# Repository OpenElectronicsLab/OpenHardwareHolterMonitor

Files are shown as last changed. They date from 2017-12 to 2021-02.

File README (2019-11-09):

OpenHardwareHolterMonitor is still in early development

This is not a medical device; it is not intended for diagnosis or treatment
of any medical condition.

http://openelectronicslab.github.io/OpenHardwareHolterMonitor/

LICENSE

Software and firmware is licensed under the GPL version 3 as published by the Free Software Foundataion or (at your option) any later version.

https://www.gnu.org/licenses/gpl-3.0.txt

Hardware designs and documentation are licnesed under the CERN Open Hardware
License version 1.1 or (at your option) any later version.

https://www.ohwr.org/licenses/cern-ohl/license_versions/v1.1

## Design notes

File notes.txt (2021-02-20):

Before we go to print again:
* eyeball review the zones and layers
  * also of the gerbers
* testability
  * what needs to be pulled out as test pads
  * non-tented vias rather than pads?
  * or run all the test to the edge of a board and have a connector?
* JTAG - learn about it?
* KiCAD
   * CI/CD design rule checks? - is it commanline scriptable
   * build KiCAD from source!
   * module community?
   * footprint default (e.g.: 0603 hand-solder), preference file?
   * smarter BoM creation?
      * crawl mouser/digikey for smart defaults for "jelly beans" ?

START HERE:
 * Boston Board has shorts in solder bridges on WROOM, fix this first.

 * Programming the board:
	- we are missing pull-up resistors for ENable (~RESET~) and IO0 (boot)
	- we have not successfully programmed the Wroom using FTDI, unless
		we also by hand toggle the EN & IO0 via jumpers or buttons
	- WROOM32 in Utrecht seems to have a bad reset button
	- Sequence to program the the Wroom:
		0) Connect FT232 USB->Serial to Wroom
			* RX0 to TXD0
			* TX0 to RXD0
			* 3v3 to Power
			* GND to GND
		1) connect IO0 to ground (or hold down boot button)
		2) connect EN to ground briefly (or press and release EN)
		3) hit upload from Arduino IDE as ESP32 Dev Module
	- To make the board go, plan is:
		* solder 10k pull-up resistors between FTDI_V and Q1, Q2
		* solder headers for jumper wires into EN and IO0
		* manually, or via an arduino, toggle the EN, IO0
		* push firmware via USB->Serial

 * Case Design
	- LEDs not considered, light pipes?
	- posts need buttressing
	- hex holes allow nuts to spin, make a tad smaller
	- screw holes are very tight, widen a tad
	- recess touch-proof connectors so they are flush with case or inside
	- compensate for some print warping?
	- gasket for where case sides join?
 * Board design: do we want a programmable LED?
	- allows power LED to be Not Installed / controlled via CPU
	- allows debug blink-codes
 * expose EN and IO0 on FTDI header (P1)?
 * label SW1 with OFF and ON

TODO THIS VERSION (v0.2):

 * double-check that our very tight pick-and-place requirements are realistic
   e.g.: R45
   https://ocmmanufacturing.com/resources/resource/dfm-tip-spacing-components-on-a-pcb/
 * Case Design
 * Software prototype on esp32

 * REV2 board required
   - FIXED in v0.2 : d'oh! v0.1 BT1 is BAT2 & BT2 is BAT1 !!!
   - FIXED in v0.2 : d'oh! v0.1 DGS and CBE are wrong on all the Qs !!!
     - (we de-soldered and rotated and/or jumped around on our v0.1 prototypes)

ORDER PROCESS:
* board dimensions units are in CM not MM at Gold Phoenix

SOMEDAY MAYBE:
  - add solder mask between pins on ADS? (conflicting recommendations)
  - north reserved pin which connects to DGND: smooth awkward copper path

FOR NEXT VERSION:
* more space around mounting holes for screw support placement
* waterproof USB connectors for dust-proofing
* check footprints for corresponding 3D models
* check footprints to see if they are current or from an older version
* Check BOM for duplicates, update schematic accordingly
  - e.g.: "R" vs. "R-device" components which are both 100K Ohm 0603.
* keep a detailed journal of decisions
* add manufacturer-partnumber and manufacturer fields before other annotations
* label all of the networks between components
* finish BOM before starting PCB

CONSIDER:
* Medical Instrument Design and Development on page 265
  suggests switching to sheilded leads for EMI
  (can we use filtering instead?)

* look at standards, determine if external clock is required

* Build a configurably "noisy" and "bad" power-supply for testing
  dial-in out-of-spec for USB: (only 3 or 4 volts or +8 volts)
  configurable amount of 50Hz or 60Hz noise

* Create test signals (configurable fake EEG readings we can feed in)

* simulate defribulator voltage added to test cardiac signals

* test vibration influence with car, train, metro, bus, bike
  compare with swapping-in a tantilum for C8

* Regulater's Capacitor C42 1uF to 10uF should be fine;
  bigger is typically better, but we may get oscillation, need to test

# NOTES ON v0.1 SOT-23 TRANSITORS WITH INCORRECT FOOTPRINTS

## KiCad SOT-23 footprint pin numbering:

      1
          3
      2

## Q1 Q2 : DSS4240T-7

    v0.1 KiCad     actual part

      E                 B
          C                 C
      B                 E

## Q3 Q4 Q5 Q6: 2N7002-7-F

    v0.1 KiCad     actual part

      D                 G
          S                 D
      G                 S

## Q7 Q8 Q9 Q10 Q11 : DMG2305UX-13

    v0.1 KiCad     actual part

      D                 G
          S                 D
      G                 S

--------------------------------------------
Alternated resistors front-to-back in order increase the clearance between
resistors.

--------------------------------------------
esp32	20mA
 +WiFi	90-260mA
ads1298	5mA
ADP7158	4mA -- just one of many low noise linear regulator
sdCard	<1mA
 write	100mA

not tx	~100-200mA
w/ tx	~500mA ... thus efficient power isolation to run off of USB

2 main batteries, but can operate from one, and can swap each out one at a time
 ... simple power-level indicator? push-button and light up to 0-to-3 LEDs?
 ... also indicate on web-page?
1 (regargeable?) coin battery for the real-time-clock
  TODO: look up coin charger schematic on Adafruit?

LP5912-3.0DRVR LDO Voltage Regulator
reference layout suggests big wide ground connecting Pin2 (NC) to thermal pad
with vias to pin 5 (GND)
and use X7R caps anywhere from 1-to-10uF
and a pullup resistor of 10k-100k for PG

charging: conisder the PCP73833 which has cell temperature monitoring
http://www.microchip.com/wwwproducts/en/en027785

18650 batteries are widely available and cost is reasonable
ADS requires 2.7 min; ESP requires 2.8v min; thus no problem.
batteries drop off dramatically around 3 volts:
http://www.candlepowerforums.com/vb/showthread.php?308451-18650-battery-test-with-capacity-curves-for-many-cells

https://www.amazon.de/Nitecore-Intellicharge-Ladeger%C3%A4t-Li-Ion-Batterien/dp/B06XFH6Z5D/ref=sr_1_1?ie=UTF8&qid=1509900684&sr=8-1&keywords=18650+charger+nitecore

https://smile.amazon.com/Battery-Li-Ion-Rechargeable-Button-LR2032/dp/B0058E94O6/ref=sr_1_sc_2?ie=UTF8&qid=1509899680&sr=8-2-spell&keywords=2032+rechagable

V=IR
R=V/I=(1.2V)/(50e-6)=2.4e4V/1A=24000 Ohm
R=V/I=(1.26V)/(47e6)

RO = (R2*RC)/(R2+RC) - (R2*RH)/(R2+RH) = (R2^2*RC - R2^2*RH)/(R2^2 + R2*RC + R2*RH + RC*RH)
R2^2 (RC - RH) = R0 * R2^2 + R0 * R2 * (RC + RH) + R0*RC*RH
0 = -R2^2 * (RC - RH) + R0 * R2^2 + R0 * R2 * (RC + RH) + R0*RC*RH
0 = (R0 - RC + RH) R2^2 + (R0 * (RC + RH)) * R2 + R0*RC*RH
0 = a * R2^2 + b * R2 + c
R2 = -b +/- sqrt(4*a*c - b^2)/(2a)

eric@titan:~/src/build-mysql-server$ python
Python 2.7.13 (default, Nov 24 2017, 17:33:09) 
[GCC 6.3.0 20170516] on linux2
Type "help", "copyright", "credits" or "license" for more information.
>>> from math import *
>>> 10e3 * exp(-3380*(1/(273.15+25.) + 1/(273.15+60))
... )
4.681859273431694e-06
>>> 10e3 * exp(-3380*(1/(273.15+25) - 1/(273.15+60)))
3039.1856851602356
>>> exp(1)
2.718281828459045
>>> exp(1)**2
7.3890560989306495
>>> exp(2)  
7.38905609893065
>>> 10e3 * exp(-3380*(1/(273.15+25) - 1/(273.15+60)))
3039.1856851602356
>>> 10e3 * exp(-3380*(1/(273.15+25) - 1/(273.15+45)))
4903.401159843523
>>> 10e3 * exp(-3380*(1/(273.15+25) - 1/(273.15+0.0)))
28223.725086022154
>>> R0 = 19e3
>>> RH = 3039.1856851602356
>>> RC = 28223.725086022154
>>> RH = 4903.401159843523
>>> b= (R0 * (RC + RH))
>>> a = (R0 - RC + RH)
>>> c =R0*RC*RH
>>> R2 = -b - sqrt(4*a*c - b^2)/(2a)
  File "<stdin>", line 1
    R2 = -b - sqrt(4*a*c - b^2)/(2a)
                                  ^
SyntaxError: invalid syntax
>>> R2 = -b - sqrt(4*a*c - b**2)/(2*a)
Traceback (most recent call last):
  File "<stdin>", line 1, in <module>
ValueError: math domain error
>>> R2 = (-b - sqrt(b**2 - 4*a*c))/(2*a)
>>> R2
149751.3160728841
>>> R2 = (-b + sqrt(b**2 - 4*a*c))/(2*a)
>>> R2
-4064.231162986638
>>> R2 = (-b - sqrt(b**2 - 4*a*c))/(2*a)
>>> R12
Traceback (most recent call last):
  File "<stdin>", line 1, in <module>
NameError: name 'R12' is not defined
>>> R2
149751.3160728841
>>> R1=(5e3 -((R2 * RH)/(R2+RH)))
>>> R1
252.0634995252176
>>> 1/( 1/(273.15 + 25) + 1/3380. * ln(24e3/10e3) )                            
Traceback (most recent call last):
  File "<stdin>", line 1, in <module>
NameError: name 'ln' is not defined
>>> 1/( 1/(273.15 + 25) + 1/3380. * log(24e3/10e3) )
276.77593699164424
>>> log(10)
2.302585092994046
>>> log(exp(1))
1.0
>>> 1/( 1/(273.15 + 25) + 1/3380. * log(24e3/10e3) ) - 273.15
3.6259369916442665
>>> 1/( 1/(273.15 + 25) + 1/3380. * log(5e3/10e3) ) - 273.15
44.416848098726064
>>> 1/( 1/(273.15 + 25) + 1/3380. * log(5e3*.99/10e3) ) - 273.15
44.71700233658754
>>> 1/( 1/(273.15 + 25) + 1/3380. * log(5e3*1.01/10e3) ) - 273.15
44.12023842251841
>>> 1/( 1/(273.15 + 25) + 1/3380. * log(5e3/10e3) ) - 273.15
44.416848098726064
>>> 1.25/50-3
-2.975
>>> 1.25/50e-3
25.0
>>> 1.25/50e-6
25000.0
>>> 1.2/50e-6
23999.999999999996
>>> 1.26/47e-6
26808.510638297874
>>> 1/( 1/(273.15 + 25) + 1/3380. * log(26808e3*1.01/10e3) ) - 273.15
-97.477943830615
>>> 1/( 1/(273.15 + 25) + 1/3380. * log(26808*1.01/10e3) ) - 273.15
0.919435923053868
>>> 1.20/53e-6
22641.509433962263
>>> 1/( 1/(273.15 + 25) + 1/3380. * log(22641*1.01/10e3) ) - 273.15
4.725901928055919
>>> 0.235/53e-6
4433.962264150943
>>> 1/( 1/(273.15 + 25) + 1/3380. * log(4434*0.99/10e3) ) - 273.15
48.34929827083289
>>> 0.265/47e-6
5638.297872340426
>>> 1/( 1/(273.15 + 25) + 1/3380. * log(5638*0.99/10e3) ) - 273.15
41.16716023313063
>>> 1/( 1/(273.15 + 25) + 1/3380. * log(5638*1.01/10e3) ) - 273.15
40.58363861408782

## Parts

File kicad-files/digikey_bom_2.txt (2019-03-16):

#,Manufacturer Part Number,Manufacturer,Description,Customer Reference,Availability,Part Status,Digi-Key Part Number,Packaging,Requested Quantity,Quantity,Unit Price,Extended Price,Manufacturer Lead Weeks,US Tariff Status
1,1043,Keystone Electronics,BATTERY HOLDER 18650 PC PIN,BT1 BT2,8660 Available,Active,36-1043-ND,BULK,2,2,2.30000,$4.60,Manufacturer Standard Lead Time 6 Weeks
2,CC0603JRX7R9BB104,Yageo,CAP CER 0.1UF 50V X7R 0603,C4 C6 C10 C13 C14 C17 C18 C22 C36 C38,668000 Available,Active,311-1779-1-ND,CT,10,10,0.09700,$0.97,Manufacturer Standard Lead Time 16 Weeks
3,CC0603JRNPO9BN101,Yageo,CAP CER 100PF 50V C0G/NPO 0603,C20,1712000 Available,Active,311-1069-1-ND,CT,1,1,0.10000,$0.10,Manufacturer Standard Lead Time 16 Weeks,Tariff Applied
4,CL10B103KB8NCNC,Samsung Electro-Mechanics,CAP CER 10000PF 50V X7R 0603,C21,6216000 Available,Active,1276-1921-1-ND,CT,1,1,0.10000,$0.10,Not Available,Tariff Applied
5,CL21B106KPQNNNE,Samsung Electro-Mechanics,CAP CER 10UF 10V X7R 0805,C12 C40 C42,1822000 Available,Active,1276-1764-1-ND,CT,3,3,0.29000,$0.87,Not Available
6,CC0603JRNPO9BN120,Yageo,CAP CER 12PF 50V C0G/NPO 0603,C1 C2,688000 Available,Active,311-1059-1-ND,CT,2,2,0.10000,$0.20,Manufacturer Standard Lead Time 16 Weeks,Tariff Applied
7,LMK107B7105KA-T,Taiyo Yuden,CAP CER 1UF 10V X7R 0603,C3 C5 C7 C9 C11 C15 C16 C19 C23,1896000 Available,Active,587-1242-1-ND,CT,9,9,0.10000,$0.90,Not Available,Tariff Applied
8,GRM21BD71A226ME44L,Murata Electronics North America,CAP CER 22UF 10V X7T 0805,C8 C39 C41,411000 Available,Active,490-9959-1-ND,CT,3,3,0.48000,$1.44,Not Available
9,TPSE337K010T0050V,AVX Corporation,CAP TANT 330UF 10% 10V 2917,C34 C35 C37,400 Available,Active,478-11252-1-ND,CT,3,3,2.45000,$7.35,Manufacturer Standard Lead Time 10 Weeks
10,C0603C471JAGAC7867,KEMET,CAP CER 470PF 250V C0G/NP0 0603,C24 C25 C26 C27 C28 C29 C30 C31 C32 C33,2701 Available,Active,399-14986-1-ND,CT,10,10,0.07600,$0.76,Manufacturer Standard Lead Time 52 Weeks
11,693072010801,Wurth Electronics Inc.,CONN MICRO SD CARD HINGED TYPE,CON1,1200 Available,Active,732-3820-1-ND,CT,1,1,3.20000,$3.20,Manufacturer Standard Lead Time 17 Weeks
12,BAT60JFILM,STMicroelectronics,DIODE SCHOTTKY 10V 3A SOD323,D1 D2 D3 D6 D10 D12 D13 D14,57000 Available,Active,497-3707-1-ND,CT,8,8,0.39000,$3.12,Manufacturer Standard Lead Time 12 Weeks,Tariff Applied
13,SS10PH10-M3/86A,Vishay Semiconductor Diodes Division,DIODE SCHOTTKY 100V 10A TO277A,D8,24000 Available,Active,SS10PH10-M3/86AGICT-ND,CT,1,1,0.74000,$0.74,Manufacturer Standard Lead Time 12 Weeks,Tariff Applied
14,SMBJ5339B-TP,Micro Commercial Co,DIODE ZENER 5.6V 5W DO214AA,D4 D5,33000 Available,Active,SMBJ5339B-TPMSCT-ND,CT,2,2,0.87000,$1.74,Not Available
15,IN-S63BTA,Inolux,LED AMBER CLEAR 0603 SMD,D7 D11,4000 Available,Active,1830-1071-1-ND,CT,2,2,0.36000,$0.72,Manufacturer Standard Lead Time 8 Weeks
16,LTST-C191KGKT,Lite-On Inc.,LED GREEN CLEAR SMD,D9,1020000 Available,Active,160-1446-1-ND,CT,1,1,0.29000,$0.29,Manufacturer Standard Lead Time 10 Weeks,Tariff Applied
17,1812L050/30PR,Littelfuse Inc.,PTC RESET FUSE 30V 500MA 1812,F1 F2,12618 Available,Active,F4159CT-ND,CT,2,2,1.04000,$2.08,Manufacturer Standard Lead Time 11 Weeks,Tariff Applied
18,CMS1-12-R,Eaton - Electronics Division,CMC 131UH 1.15A 2LN SMD,FL1,2000 Available,Active,513-1683-1-ND,CT,1,1,2.95000,$2.95,Manufacturer Standard Lead Time 16 Weeks
19,M50-3000645,Harwin Inc.,CONN RCPT 12POS 0.05 GOLD PCB,J1,2703 Available,Active,952-1366-5-ND,TUBE,1,1,1.70000,$1.70,Manufacturer Standard Lead Time 10 Weeks
20,12401610E4#2A,Amphenol ICC (Commercial Products),CONN RCP USB3.1 TYPEC 24P SMD RA,J13,37680 Available,Active,12401610E4#2ACT-ND,CT,1,1,2.24000,$2.24,Manufacturer Standard Lead Time 12 Weeks,Tariff Applied
21,629105150521,Wurth Electronics Inc.,CONN RCPT USB2.0 MICRO B SMD R/A,J12,4400 Available,Active,732-5960-1-ND,CT,1,1,2.07000,$2.07,Manufacturer Standard Lead Time 11 Weeks
22,61300711121,Wurth Electronics Inc.,CONN HEADER VERT 7POS 2.54MM,P1,6236 Available,Active,732-5320-ND,BAG,1,1,0.37000,$0.37,Manufacturer Standard Lead Time 14 Weeks
23,2N7002-7-F,Diodes Incorporated,MOSFET N-CH 60V 115MA SOT23-3,Q3 Q4,6681000 Available,Active,2N7002-FDICT-ND,CT,2,2,0.22000,$0.44,Not Available,Tariff Applied
24,2N7002-7-F,Diodes Incorporated,MOSFET N-CH 60V 115MA SOT23-3,Q5 Q6,6681000 Available,Active,2N7002-FDICT-ND,CT,2,2,0.22000,$0.44,Not Available,Tariff Applied
25,DMG2305UX-13,Diodes Incorporated,MOSFET P-CH 20V 4.2A SOT23,Q7 Q8 Q9 Q10 Q11,879607 Available,Active,DMG2305UX-13DICT-ND,CT,5,5,0.45000,$2.25,Manufacturer Standard Lead Time 20 Weeks,Tariff Applied
26,DSS4240T-7,Diodes Incorporated,TRANS NPN 40V 2A SOT-23,Q1 Q2,420000 Available,Active,DSS4240TDICT-ND,CT,2,2,0.44000,$0.88,Manufacturer Standard Lead Time 20 Weeks,Tariff Applied
27,RC0603FR-070RL,Yageo,RES SMD 0 OHM JUMPER 1/10W 0603,R31 R32,4235000 Available,Active,311-0.0HRCT-ND,CT,2,2,0.10000,$0.20,Manufacturer Standard Lead Time 16 Weeks,Tariff Applied
28,ERA-3AEB104V,Panasonic Electronic Components,RES SMD 100K OHM 0.1% 1/10W 0603,R7 R10 R13 R27 R28,1490000 Available,Active,P100KDBCT-ND,CT,5,5,0.35000,$1.75,Manufacturer Standard Lead Time 23 Weeks
29,ERA-3AEB104V,Panasonic Electronic Components,RES SMD 100K OHM 0.1% 1/10W 0603,R37 R38 R41 R42 R43,1490000 Available,Active,P100KDBCT-ND,CT,5,5,0.35000,$1.75,Manufacturer Standard Lead Time 23 Weeks
30,ERT-J1VG103JA,Panasonic Electronic Components,THERMISTOR NTC 10KOHM 3380K 0603,R33 R34,52000 Available,Active,P12014CT-ND,CT,2,2,0.18000,$0.36,Manufacturer Standard Lead Time 7 Weeks
31,ERJ-PB3B1202V,Panasonic Electronic Components,RES SMD 12K OHM 0.1% 1/5W 0603,R5 R6,500 Available,Active,P20094CT-ND,CT,2,2,0.25000,$0.50,Manufacturer Standard Lead Time 18 Weeks
32,ERJ-PB3B1001V,Panasonic Electronic Components,RES SMD 1K OHM 0.1% 1/5W 0603,R9 R12 R35 R36,40000 Available,Active,P19972CT-ND,CT,4,4,0.25000,$1.00,Manufacturer Standard Lead Time 18 Weeks
33,ERJ-PB3B3901V,Panasonic Electronic Components,RES SMD 3.9K OHM 0.1% 1/5W 0603,R8 R11,5000 Available,Active,P20038CT-ND,CT,2,2,0.25000,$0.50,Manufacturer Standard Lead Time 18 Weeks
34,ERA-3AEB331V,Panasonic Electronic Components,RES SMD 330 OHM 0.1% 1/10W 0603,R39 R40,55000 Available,Active,P330DBCT-ND,CT,2,2,0.35000,$0.70,Manufacturer Standard Lead Time 23 Weeks
35,RN73C1J392KBTD,TE Connectivity Passive Product,RES SMD 392K OHM 0.1% 1/16W 0603,R16,3759 Available,Active,A124746CT-ND,CT,1,1,0.80000,$0.80,Manufacturer Standard Lead Time 9 Weeks
36,ERA-3AEB470V,Panasonic Electronic Components,RES SMD 47 OHM 0.1% 1/10W 0603,R1 R2 R3 R4 R14 R15,115000 Available,Active,P47DBCT-ND,CT,6,6,0.35000,$2.10,Manufacturer Standard Lead Time 23 Weeks
37,ERJ-PB3B5101V,Panasonic Electronic Components,RES SMD 5.1K OHM 0.1% 1/5W 0603,R29 R30,5000 Available,Active,P20052CT-ND,CT,2,2,0.25000,$0.50,Manufacturer Standard Lead Time 18 Weeks
38,ASRM2JA51K0,Stackpole Electronics Inc,RES 51K OHM 2W 5% AXIAL,R17 R18 R19 R20 R21 R22 R23 R24 R25 R26,229 Available,Active,ASRM2JA51K0CT-ND,CT,10,10,0.57800,$5.78,Manufacturer Standard Lead Time 11 Weeks
39,JS102011SAQN,C&K,SWITCH SLIDE SPDT 300MA 6V,SW1,36000 Available,Active,401-1999-1-ND,CT,1,1,0.59000,$0.59,Manufacturer Standard Lead Time 13 Weeks,Tariff Applied
40,ADS1298IPAG,Texas Instruments,IC AFE 24BIT SPI 32KSPS 64TQFP,U2,5197 Available,Active,296-27734-ND,TRAY,1,1,38.99000,$38.99,Manufacturer Standard Lead Time 12 Weeks
41,ESP-32,RF Solutions,WIFI802.11B/G/N/E/I BLEUTOOTH CL,U1,7 Available,Active,ESP-32-ND,BAG,1,1,15.68000,$15.68,Manufacturer Standard Lead Time 4 Weeks
42,LP5912-3.3DRVT,Texas Instruments,IC REG LINEAR 3.3V 500MA 6SON,U6,6500 Available,Active,296-44153-1-ND,CT,1,1,1.38000,$1.38,Manufacturer Standard Lead Time 8 Weeks
43,MCP73833T-AMI/UN,Microchip Technology,IC LI-ION/LI-POLY CTRLR 10MSOP,U3 U4,17500 Available,Active,MCP73833T-AMI/UNCT-ND,CT,2,2,0.88000,$1.76,Manufacturer Standard Lead Time 6 Weeks
44,REM3-0505S/A,Recom Power,DC DC CONVERTER 5V 3W,U7,425 Available,Active,945-2224-ND,TUBE,1,1,52.54000,$52.54,Manufacturer Standard Lead Time 16 Weeks
45,TPS2113APWR,Texas Instruments,IC OR CTRLR SRC SELECT 8TSSOP,U5,30606 Available,Active,296-16938-1-ND,CT,1,1,2.41000,$2.41,Manufacturer Standard Lead Time 8 Weeks
46,FK161EIHM0.032768-T5,Fox Electronics,CRYSTAL 32.768KHZ 12.5PF SMD,Y1,5754 Available,Active,631-1486-1-ND,CT,1,1,1.91000,$1.91,Manufacturer Standard Lead Time 13 Weeks

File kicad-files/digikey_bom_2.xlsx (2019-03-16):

# | Manufacturer Part Number | Manufacturer | Description | Customer Reference | Digi-Key Part Number | Quantity/board | Quantity Extra | Quantity
1 | 1043 | Keystone Electronics | BATTERY HOLDER 18650 PC PIN | BT1 BT2 | 36-1043-ND | 2 | 1 | 13
2 | CC0603JRX7R9BB104 | Yageo | CAP CER 0.1UF 50V X7R 0603 | C4 C6 C10 C13 C14 C17 C18 C22 C36 C38 | 311-1779-1-ND | 10 | 5 | 65
3 | CC0603JRNPO9BN101 | Yageo | CAP CER 100PF 50V C0G/NPO 0603 | C20 | 311-1069-1-ND | 1 | 5 | 11
4 | CL10B103KB8NCNC | Samsung Electro-Mechanics | CAP CER 10000PF 50V X7R 0603 | C21 | 1276-1921-1-ND | 1 | 5 | 11
5 | CL21B106KPQNNNE | Samsung Electro-Mechanics | CAP CER 10UF 10V X7R 0805 | C12 C40 C42 | 1276-1764-1-ND | 3 | 5 | 23
6 | CC0603JRNPO9BN120 | Yageo | CAP CER 12PF 50V C0G/NPO 0603 | C1 C2 | 311-1059-1-ND | 2 | 5 | 17
7 | LMK107B7105KA-T | Taiyo Yuden | CAP CER 1UF 10V X7R 0603 | C3 C5 C7 C9 C11 C15 C16 C19 C23 | 587-1242-1-ND | 9 | 5 | 59
8 | GRM21BD71A226ME44L | Murata Electronics North America | CAP CER 22UF 10V X7T 0805 | C8 C39 C41 | 490-9959-1-ND | 3 | 5 | 23
9 | TPSE337K010T0050V | AVX Corporation | CAP TANT 330UF 10% 10V 2917 | C34 C35 C37 | 478-11252-1-ND | 3 | 5 | 23
10 | C0603C471JAGAC7867 | KEMET | CAP CER 470PF 250V C0G/NP0 0603 | C24 C25 C26 C27 C28 C29 C30 C31 C32 C33 | 399-14986-1-ND | 10 | 5 | 65
11 | 693072010801 | Wurth Electronics Inc. | CONN MICRO SD CARD HINGED TYPE | CON1 | 732-3820-1-ND | 1 | 1 | 7
12 | BAT60JFILM | STMicroelectronics | DIODE SCHOTTKY 10V 3A SOD323 | D1 D2 D3 D6 D10 D12 D13 D14 | 497-3707-1-ND | 8 | 5 | 53
13 | SS10PH10-M3/86A | Vishay Semiconductor Diodes Division | DIODE SCHOTTKY 100V 10A TO277A | D8 | SS10PH10-M3/86AGICT-ND | 1 | 5 | 11
14 | SMBJ5339B-TP | Micro Commercial Co | DIODE ZENER 5.6V 5W DO214AA | D4 D5 | SMBJ5339B-TPMSCT-ND | 2 | 5 | 17
15 | IN-S63BTA | Inolux | LED AMBER CLEAR 0603 SMD | D7 D11 | 1830-1071-1-ND | 2 | 5 | 17
16 | LTST-C191KGKT | Lite-On Inc. | LED GREEN CLEAR SMD | D9 | 160-1446-1-ND | 1 | 5 | 11
17 | 1812L050/30PR | Littelfuse Inc. | PTC RESET FUSE 30V 500MA 1812 | F1 F2 | F4159CT-ND | 2 | 5 | 17
18 | CMS1-12-R | Eaton - Electronics Division | CMC 131UH 1.15A 2LN SMD | FL1 | 513-1683-1-ND | 1 | 5 | 11
19 | M50-3000645 | Harwin Inc. | CONN RCPT 12POS 0.05 GOLD PCB | J1 | 952-1366-5-ND | 1 | 1 | 7
20 | 12401610E4#2A | Amphenol ICC (Commercial Products) | CONN RCP USB3.1 TYPEC 24P SMD RA | J13 | 12401610E4#2ACT-ND | 1 | 1 | 7
21 | 629105150521 | Wurth Electronics Inc. | CONN RCPT USB2.0 MICRO B SMD R/A | J12 | 732-5960-1-ND | 1 | 1 | 7
22 | 61300711121 | Wurth Electronics Inc. | CONN HEADER VERT 7POS 2.54MM | P1 | 732-5320-ND | 1 | 1 | 7
23 | 2N7002-7-F | Diodes Incorporated | MOSFET N-CH 60V 115MA SOT23-3 | Q3 Q4 | 2N7002-FDICT-ND | 2 | 5 | 17
24 | 2N7002-7-F | Diodes Incorporated | MOSFET N-CH 60V 115MA SOT23-3 | Q5 Q6 | 2N7002-FDICT-ND | 2 | 5 | 17
25 | DMG2305UX-13 | Diodes Incorporated | MOSFET P-CH 20V 4.2A SOT23 | Q7 Q8 Q9 Q10 Q11 | DMG2305UX-13DICT-ND | 5 | 5 | 35
26 | DSS4240T-7 | Diodes Incorporated | TRANS NPN 40V 2A SOT-23 | Q1 Q2 | DSS4240TDICT-ND | 2 | 5 | 17
27 | RC0603FR-070RL | Yageo | RES SMD 0 OHM JUMPER 1/10W 0603 | R31 R32 | 311-0.0HRCT-ND | 2 | 5 | 17
28 | ERA-3AEB104V | Panasonic Electronic Components | RES SMD 100K OHM 0.1% 1/10W 0603 | R7 R10 R13 R27 R28 | P100KDBCT-ND | 5 | 5 | 35
29 | ERA-3AEB104V | Panasonic Electronic Components | RES SMD 100K OHM 0.1% 1/10W 0603 | R37 R38 R41 R42 R43 | P100KDBCT-ND | 5 | 5 | 35
30 | ERT-J1VG103JA | Panasonic Electronic Components | THERMISTOR NTC 10KOHM 3380K 0603 | R33 R34 | P12014CT-ND | 2 | 5 | 17
31 | ERJ-PB3B1202V | Panasonic Electronic Components | RES SMD 12K OHM 0.1% 1/5W 0603 | R5 R6 | P20094CT-ND | 2 | 5 | 17
32 | ERJ-PB3B1001V | Panasonic Electronic Components | RES SMD 1K OHM 0.1% 1/5W 0603 | R9 R12 R35 R36 | P19972CT-ND | 4 | 5 | 29
33 | ERJ-PB3B3901V | Panasonic Electronic Components | RES SMD 3.9K OHM 0.1% 1/5W 0603 | R8 R11 | P20038CT-ND | 2 | 5 | 17
34 | ERA-3AEB331V | Panasonic Electronic Components | RES SMD 330 OHM 0.1% 1/10W 0603 | R39 R40 | P330DBCT-ND | 2 | 5 | 17
35 | RN73C1J392KBTD | TE Connectivity Passive Product | RES SMD 392K OHM 0.1% 1/16W 0603 | R16 | A124746CT-ND | 1 | 5 | 11
36 | ERA-3AEB470V | Panasonic Electronic Components | RES SMD 47 OHM 0.1% 1/10W 0603 | R1 R2 R3 R4 R14 R15 | P47DBCT-ND | 6 | 5 | 41
37 | ERJ-PB3B5101V | Panasonic Electronic Components | RES SMD 5.1K OHM 0.1% 1/5W 0603 | R29 R30 | P20052CT-ND | 2 | 5 | 17
38 | ASRM2JA51K0 | Stackpole Electronics Inc | RES 51K OHM 2W 5% AXIAL | R17 R18 R19 R20 R21 R22 R23 R24 R25 R26 | ASRM2JA51K0CT-ND | 10 | 5 | 65
39 | JS102011SAQN | C&K | SWITCH SLIDE SPDT 300MA 6V | SW1 | 401-1999-1-ND | 1 | 1 | 7
40 | ADS1298IPAG | Texas Instruments | IC AFE 24BIT SPI 32KSPS 64TQFP | U2 | 296-27734-ND | 1 | 1 | 7
41 | ESP-32 | RF Solutions | WIFI802.11B/G/N/E/I BLEUTOOTH CL | U1 | ESP-32-ND | 1 | 1 | 7
42 | LP5912-3.3DRVT | Texas Instruments | IC REG LINEAR 3.3V 500MA 6SON | U6 | 296-44153-1-ND | 1 | 1 | 7
43 | MCP73833T-AMI/UN | Microchip Technology | IC LI-ION/LI-POLY CTRLR 10MSOP | U3 U4 | MCP73833T-AMI/UNCT-ND | 2 | 1 | 13
44 | REM3-0505S/A | Recom Power | DC DC CONVERTER 5V 3W | U7 | 945-2224-ND | 1 | 1 | 7
45 | TPS2113APWR | Texas Instruments | IC OR CTRLR SRC SELECT 8TSSOP | U5 | 296-16938-1-ND | 1 | 1 | 7
46 | FK161EIHM0.032768-T5 | Fox Electronics | CRYSTAL 32.768KHZ 12.5PF SMD | Y1 | 631-1486-1-ND | 1 | 1 | 7
47 |  |  | NI | J2 J3 J4 J5 J6 J7 J8 J9 J10 J11 |  | 0 | 0 | 0
48 |  |  | NI | TH1 TH2 |  | 0 | 0 | 0

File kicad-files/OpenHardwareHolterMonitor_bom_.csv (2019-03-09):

Component | Description | Part | References | Value | Footprint | Quantity Per PCB | Datasheet | ManufacturerName | manufacturer-pn
1 |  | Battery_Cell | BT1 BT2 | Battery_Cell | Keystone1043 | 2 |  | Keystone | 1043
2 |  | C | C4 C6 C10 C13 C14 C17 C18 C22 C36 C38 | 100nF | C_0603_HandSoldering | 10 |  | Yageo | CC0603JRX7R9BB104
3 |  | C | C20 | 100pF | C_0603_HandSoldering | 1 |  | Yageo | CC0603JRNPO9BN101
4 |  | C | C21 | 10nF | C_0603_HandSoldering | 1 |  | Samsung Electro-Mechanics | CL10B103KB8NCNC
5 |  | C | C12 C40 C42 | 10uF | C_0805_HandSoldering | 3 |  | Samsung Electro-Mechanics | CL21B106KPQNNNE
6 |  | C | C1 C2 | 12pF | C_0603_HandSoldering | 2 |  | Yageo | CC0603JRNPO9BN120
7 |  | C | C3 C5 C7 C9 C11 C15 C16 C19 C23 | 1uF | C_0603_HandSoldering | 9 |  | Taiyo Yuden | LMK107B7105KA-T
8 |  | C | C8 C39 C41 | 22uF | C_0805_HandSoldering | 3 |  | Murata Electronics | GRM21BD71A226ME44L
9 |  | CP | C34 C35 C37 | 330uF | CP_Tantalum_Case-E_EIA-7260-38_Hand | 3 |  | AVX | TPSE337K010T0050V
10 |  | C | C24 C25 C26 C27 C28 C29 C30 C31 C32 C33 | 470pF | C_0603_HandSoldering | 10 |  | Yageo | CC0603JRNPOYBN471
11 |  | Micro_SD_Card | CON1 | Micro_SD_Card | MicroSd_Wurth_693072010801 | 1 |  | Wurth | 693072010801
12 |  | D_Schottky | D1 D2 D3 D6 D10 D12 D13 D14 | D_Schottky | D_SOD-323_HandSoldering | 8 |  | STMicroelectronics | BAT60JFILM
13 |  | D_Schottky_AAK | D8 | D_Schottky_AAK | TO-277A | 1 |  | Vishay | SS10PH10-M3/86A
14 |  | D_Zener | D4 D5 | D_Zener | D_SMB_Handsoldering | 2 |  | Micro Commercial Components (MCC) | SMBJ5339B-TP
15 |  | LED-device | D7 D11 | LED | LED_0603_HandSoldering | 2 | ~ | Inolux | IN-S63BTA
16 |  | LED | D9 | LED | LED_0603_HandSoldering | 1 |  | Lite-On Inc. | LTST-C191KGKT
17 |  | Polyfuse | F1 F2 | Polyfuse | R_1812_HandSoldering | 2 |  | Littelfuse | 1812L050/60MR
18 |  | EMI_Filter_LL | FL1 | 131uH | CMS1 | 1 |  | Eaton | CMS1-12-R
19 |  | Conn_01x01 | J2 J3 J4 J5 J6 J7 J8 J9 J10 J11 | Conn_01x01 | PlasticsOne_41828 | 10 |  | PlasticsOne | 41828
20 |  | Conn_02x06_Odd_Even-Connector | J1 | Conn_02x06_Odd_Even | Pin_Header_Straight_2x06_Pitch1.27mm | 1 | ~ | Harwin | M50-3000645
21 |  | USB_C_Receptacle | J13 | USB_C_Receptacle | USB_C_Receptacle_Amphenol_12401610E4-2A_CircularHoles | 1 |  | Amphenol | 12401610E4#2A
22 |  | USB_OTG | J12 | USB_OTG | USB_Micro-B_Wuerth-629105150521_CircularHoles | 1 |  | Wurth | 629105150521
23 |  | CONN_01X07 | P1 | Custom_FTDI | Pin_Header_Straight_1x07_Pitch2.54mm | 1 |  | Wurth | 61300711121
24 |  | Q_NMOS_DGS | Q3 Q4 | Q_NMOS_DGS | SOT-23W_Handsoldering | 2 |  | Diodes Incorporated | 2N7002-7-F
25 |  | Q_NMOS_DGS-device | Q5 Q6 | Q_NMOS_DGS | SOT-23W_Handsoldering | 2 |  | Diodes Incorporated | 2N7002-7-F
26 |  | Q_PMOS_DGS-device | Q7 Q8 Q9 Q10 Q11 | Q_PMOS_DGS | SOT-23_Handsoldering | 5 |  | Diodes Incorporated | DMG2305UX
27 |  | S8050 | Q1 Q2 | S8050 | SOT-23_Handsoldering | 2 |  | Diodes Incorporated | DSS4240T-7
28 |  | R | R31 R32 | 0 | R_0603_HandSoldering | 2 |  | Yageo | RC0603FR-070RL
29 |  | R | R7 R10 R13 R27 R28 | 100k | R_0603_HandSoldering | 5 |  | Panasonic Electronic Components | ERA-3AEB104V
30 |  | R-device | R37 R38 R41 R42 R43 | 100k | R_0603_HandSoldering | 5 |  | Panasonic Electronic Components | ERA-3AEB104V
31 |  | R | R33 R34 | 10K-NTC | R_0603_HandSoldering | 2 |  | Panasonic Electronic Components | ERT-J1VG103JA
32 |  | R | R5 R6 | 12K | R_0603_HandSoldering | 2 |  | Panasonic Electronic Components | ERJ-PB3B1202V
33 |  | R | R9 R12 R35 R36 | 1k | R_0603_HandSoldering | 4 |  | Panasonic Electronic Components | ERJ-PB3B1001V
34 |  | R | R8 R11 | 3.9k | R_0603_HandSoldering | 2 |  | Panasonic Electronic Components | ERJ-PB3B3901V
35 |  | R-device | R39 R40 | 330 | R_0603_HandSoldering | 2 |  | Panasonic Electronic Components | ERA-3AEB331V
36 |  | R | R16 | 392k | R_0603_HandSoldering | 1 |  | TE Connectivity Passive Product | RN73C1J392KBTD
37 |  | R | R1 R2 R3 R4 R14 R15 | 47 | R_0603_HandSoldering | 6 |  | Panasonic Electronic Components | ERA-3AEB470V
38 |  | R | R29 R30 | 5.1k | R_0603_HandSoldering | 2 |  | Panasonic Electronic Components | ERJ-PB3B5101V
39 |  | R | R17 R18 R19 R20 R21 R22 R23 R24 R25 R26 | 51k | R_Axial_Power_L20.0mm_W6.4mm_P25.40mm | 10 |  | Stackpole Electronics | ASRM2JA51K0
40 | Switch, single pole double throw | SW_SPDT | SW1 | SW_SPDT | SW_SPDT_CK-JS102011SAQN | 1 |  | C&K | JS102011SAQN
41 |  | Thermistor_NTC | TH1 TH2 | NI | CP_Radial_D4.0mm_P1.50mm | 2
42 |  | ADS1298 | U2 | ADS1298 | LQFP-64_10x10mm_Pitch0.5mm | 1 |  | Texas Instruments | ADS1298IPAG
43 |  | ESP-WROOM-32 | U1 | ESP-WROOM-32 | MODULE_ESP-WROOM-32 | 1 |  | RF Solutions | ESP-32
44 |  | LP5912 | U6 | LP5912 | WSON-6_2x2mm_Pitch0.65mm | 1 |  | Texas Instruments | LP5912-3.3DRVT
45 |  | MCP73833 | U3 U4 | MCP73833 | MSOP-10_3x3mm_Pitch0.5mm | 2 |  | Microchip Technology | MCP73833T-AMI/UN
46 |  | REM_3-xxxxS | U7 | REM_3-xxxxS | REM3 | 1 |  | Recom Power | REM3-0505S/A
47 |  | TPS2113A | U5 | TPS2113A | TSSOP-8_4.4x3mm_Pitch0.65mm | 1 |  | Texas Instruments | TPS2113A
48 |  | Crystal | Y1 | 32768Hz | K161 | 1 |  | Fox | FK161EIHM0.032768
Component Groups: | 48
Component Count: | 141
Fitted Components: | 141
Number of PCBs: | 1
Total components: | 141
Schematic Version:
Schematic Date:
BoM Date: | Sat 09 Mar 2019 03:22:51 PM CET
Schematic Source: | /home/eric/src/OpenHardwareHolterMonitor/kicad-files/OpenHardwareHolterMonitor.sch
KiCad Version: | Eeschema 5.0.2+dfsg1-1

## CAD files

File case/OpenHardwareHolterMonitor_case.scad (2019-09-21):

/* CERN OpenHardware License 1.2 */
/* OpenElectronicsLab */

/* bounding */
$fn=60; /* fixed number of fragments in 360 degrees */
side_overcut = 1;

millimeters_per_inch = 25.4;
pcb_size_x = 131;
pcb_size_y = 80;
pcb_size_z = 0.062 * millimeters_per_inch;

hole_x_positions =  [6.5,14,119,119];
hole_y_positions =  [23.5,65.5,8,72];

keepout_thickness_per_side = 7.0;
touchproof_receptacle_size_z = 6.4;

module touch_proof_receptacle() {
    union() {
        hole_center_to_box_front = 11.4;
        hole_center_to_box_back = 2.15;  // guess (no dimension given on drawing)
        touch_proof_clearance = 0.5;
        hole_center_to_cylinder_front = 11.4 + 6;
        box_width = 7.9;
        translate([hole_center_to_box_back,  -box_width/2, 0])
            cube([hole_center_to_box_front - hole_center_to_box_back, box_width,
                touchproof_receptacle_size_z + touch_proof_clearance]);
        translate([hole_center_to_box_back, 0, touchproof_receptacle_size_z/2])
            rotate([0,90,0])
            cylinder(h=hole_center_to_cylinder_front - hole_center_to_box_back,
                d=touchproof_receptacle_size_z + 2*touch_proof_clearance);
    }
}


module pcb_model() {
    board_dimensions = [pcb_size_x, pcb_size_y, pcb_size_z];
    hole_d = 2.2;
    hole_h = board_dimensions[2]+(2*side_overcut);

    difference() {
        cube(board_dimensions);
        for (i = [0:len(hole_x_positions)-1]) {
            translate([hole_x_positions[i],hole_y_positions[i],-side_overcut])
            cylinder(d=hole_d, h=hole_h);
        }
    }
}


module component_keepout_model_top() {
    keepout_dimensions = [pcb_size_x, pcb_size_y, keepout_thickness_per_side];
    hole_d = 4;
    hole_h = keepout_thickness_per_side + 2*(side_overcut);

     translate([0,0,pcb_size_z])
    difference() {
        cube(keepout_dimensions);
        // screw holes
        for (i = [0:len(hole_x_positions)-1]) {
            translate([hole_x_positions[i],hole_y_positions[i],-side_overcut])
            cylinder(d=hole_d, h=hole_h);
        }
    }
}

module component_keepout_model_bottom() {
    keepout_dimensions = [pcb_size_x, pcb_size_y, keepout_thickness_per_side];
    hole_d = 4;
    hole_h = keepout_thickness_per_side + 2*(side_overcut);

    head_hole_d = 9;
    head_hole_h = hole_h - (side_overcut +3);

    translate([0,0,-keepout_thickness_per_side])
    difference() {
        cube(keepout_dimensions);
        // screw holes
        for (i = [0:len(hole_x_positions)-1]) {
            translate([hole_x_positions[i],hole_y_positions[i],-side_overcut])
            cylinder(d=hole_d, h=hole_h);

            translate([hole_x_positions[i],hole_y_positions[i],-side_overcut])
            cylinder(d=head_hole_d, h=head_hole_h);
        }
    }
}


battery_size_z = 22 - pcb_size_z;
battery_size_x = 45;
battery_size_y = 78;
battery_position_x = 42;
battery_position_y = 1;

module batteries() {
    translate ([battery_position_x, battery_position_y, pcb_size_z])
        cube([battery_size_x, battery_size_y,battery_size_z]);
}


module touch_proof_receptacles() {
    touch_proof_receptacle_spacing = 8;
    num_touch_proof_receptacles = 10;
    for (i = [0:num_touch_proof_receptacles - 1]) {
        translate([119, 4+ (i*touch_proof_receptacle_spacing), pcb_size_z])
            touch_proof_receptacle();
    }
}

module dc_to_dc_converter() {
    dc_to_dc_position_x = 14.5;
    dc_to_dc_position_y = 20;
    dc_to_dc_position_z = pcb_size_z;
    dc_to_dc_size_x = 22;
    dc_to_dc_size_y = 33;
    dc_to_dc_height = 11;

    translate ([dc_to_dc_position_x, dc_to_dc_position_y, dc_to_dc_position_z])
        cube([dc_to_dc_size_x, dc_to_dc_size_y, dc_to_dc_height]);
}

module display_pins() {
    display_pins_pitch = 0.1 * millimeters_per_inch;
    display_pins_size_x = 1 * display_pins_pitch;
    display_pins_size_y = 7 * display_pins_pitch;
    display_pins_size_z = 10;
    display_pins_position_x = 33.5 - (display_pins_pitch/2);
    display_pins_position_y = 2 - (display_pins_pitch/2);
    display_pins_position_z = pcb_size_z;

    translate ([display_pins_position_x, display_pins_position_y, display_pins_position_z])
        cube([display_pins_size_x, display_pins_size_y, display_pins_size_z]);
}

module usb_c_connector() {
    usb_c_size_x = 11.5;
    usb_c_size_y = 20; // placeholder
    usb_c_metal_size_z = 2.5;
    usb_c_connector_clearance_z = 2.0;
    usb_c_standoff = 0.21;
    usb_c_size_z = usb_c_metal_size_z +(2 * usb_c_connector_clearance_z);
    usb_c_position_x = 6.5 - (usb_c_size_x/2);
    usb_c_position_y = pcb_size_y - usb_c_size_y/2;
    usb_c_position_z = -(usb_c_standoff + usb_c_metal_size_z + usb_c_connector_clearance_z);

    translate([usb_c_position_x, usb_c_position_y, usb_c_position_z ])
        cube([usb_c_size_x, usb_c_size_y, usb_c_size_z]);
}

module usb_micro_connector() {
    usb_micro_size_x = 10;
    usb_micro_size_y = 20; // placeholder
    usb_micro_metal_size_z = 1.8;
    usb_micro_connector_clearance_z = 2.7;
    usb_micro_standoff = 0.21;
    usb_micro_size_z = usb_micro_metal_size_z +(2 * usb_micro_connector_clearance_z);
    usb_micro_position_x = 29.5 - (usb_micro_size_x/2);
    usb_micro_position_y = pcb_size_y - usb_micro_size_y/2;
    usb_micro_position_z = -(usb_micro_standoff + usb_micro_metal_size_z + usb_micro_connector_clearance_z);

    translate([usb_micro_position_x, usb_micro_position_y, usb_micro_position_z ])
        cube([usb_micro_size_x, usb_micro_size_y, usb_micro_size_z]);
}

module power_switch() {
    switch_size_x = 4;
    switch_size_y = 20;
    switch_tab_size_z = 2;
    switch_size_z = 6 - pcb_size_z;
    switch_position_x = 47.35 - (switch_size_x/2);
    switch_position_y = pcb_size_y - switch_size_y/2;
    switch_position_z = -switch_size_z;

    translate([switch_position_x, switch_position_y, switch_position_z ])
        cube([switch_size_x, switch_size_y, switch_size_z]);
}

module board_keepout() {
    pcb_clearance_z = 0.1;
    union() {
        translate([0,0, -pcb_clearance_z/2])  pcb_model();
        translate([0,0,  pcb_clearance_z/2])  pcb_model();
        batteries();
        touch_proof_receptacles();
        dc_to_dc_converter();
        component_keepout_model_top();
        component_keepout_model_bottom();
        display_pins();
        usb_c_connector();
        usb_micro_connector();
        power_switch();
    }
}

wall_thickness = 2;
case_clearance = 0.75;
case_size_x = pcb_size_x + 2*wall_thickness + 2*case_clearance;
case_size_y = pcb_size_y + 2*wall_thickness + 2*case_clearance;
case_size_z = keepout_thickness_per_side + 22 + 2*wall_thickness + 2*case_clearance;
//echo(case_size_z);

case_screw_length = 20;
case_screw_hole_diameter = 2.3;
case_screw_countersink_diameter = 5;
case_screw_countersink_depth = 2;
case_nut_countersink_diameter  = 4 *(2 / sqrt(3)) + 0.5;
case_nut_countersink_depth  = case_size_z - case_screw_countersink_depth - case_screw_length + 1;
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

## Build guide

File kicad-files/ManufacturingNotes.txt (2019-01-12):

## Resistor placement

The 51k resistors must be placed on edge or on alternating sides of the board.

## Through hole components

Through hole components are to be placed on the opposite side of the board
from the surface mount components.

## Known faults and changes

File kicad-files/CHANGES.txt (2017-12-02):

If you are distributing a modified version of the project, please use this file
to describe the dates and details of your modifications (as described in
section 3.3b of the CERN open hardware license).  If you are using a publicly
available repository to track changes (which we encourage), you may simply list
the URL of the repository here.

https://github.com/OpenElectronicsLab/OpenHardwareHolterMonitor

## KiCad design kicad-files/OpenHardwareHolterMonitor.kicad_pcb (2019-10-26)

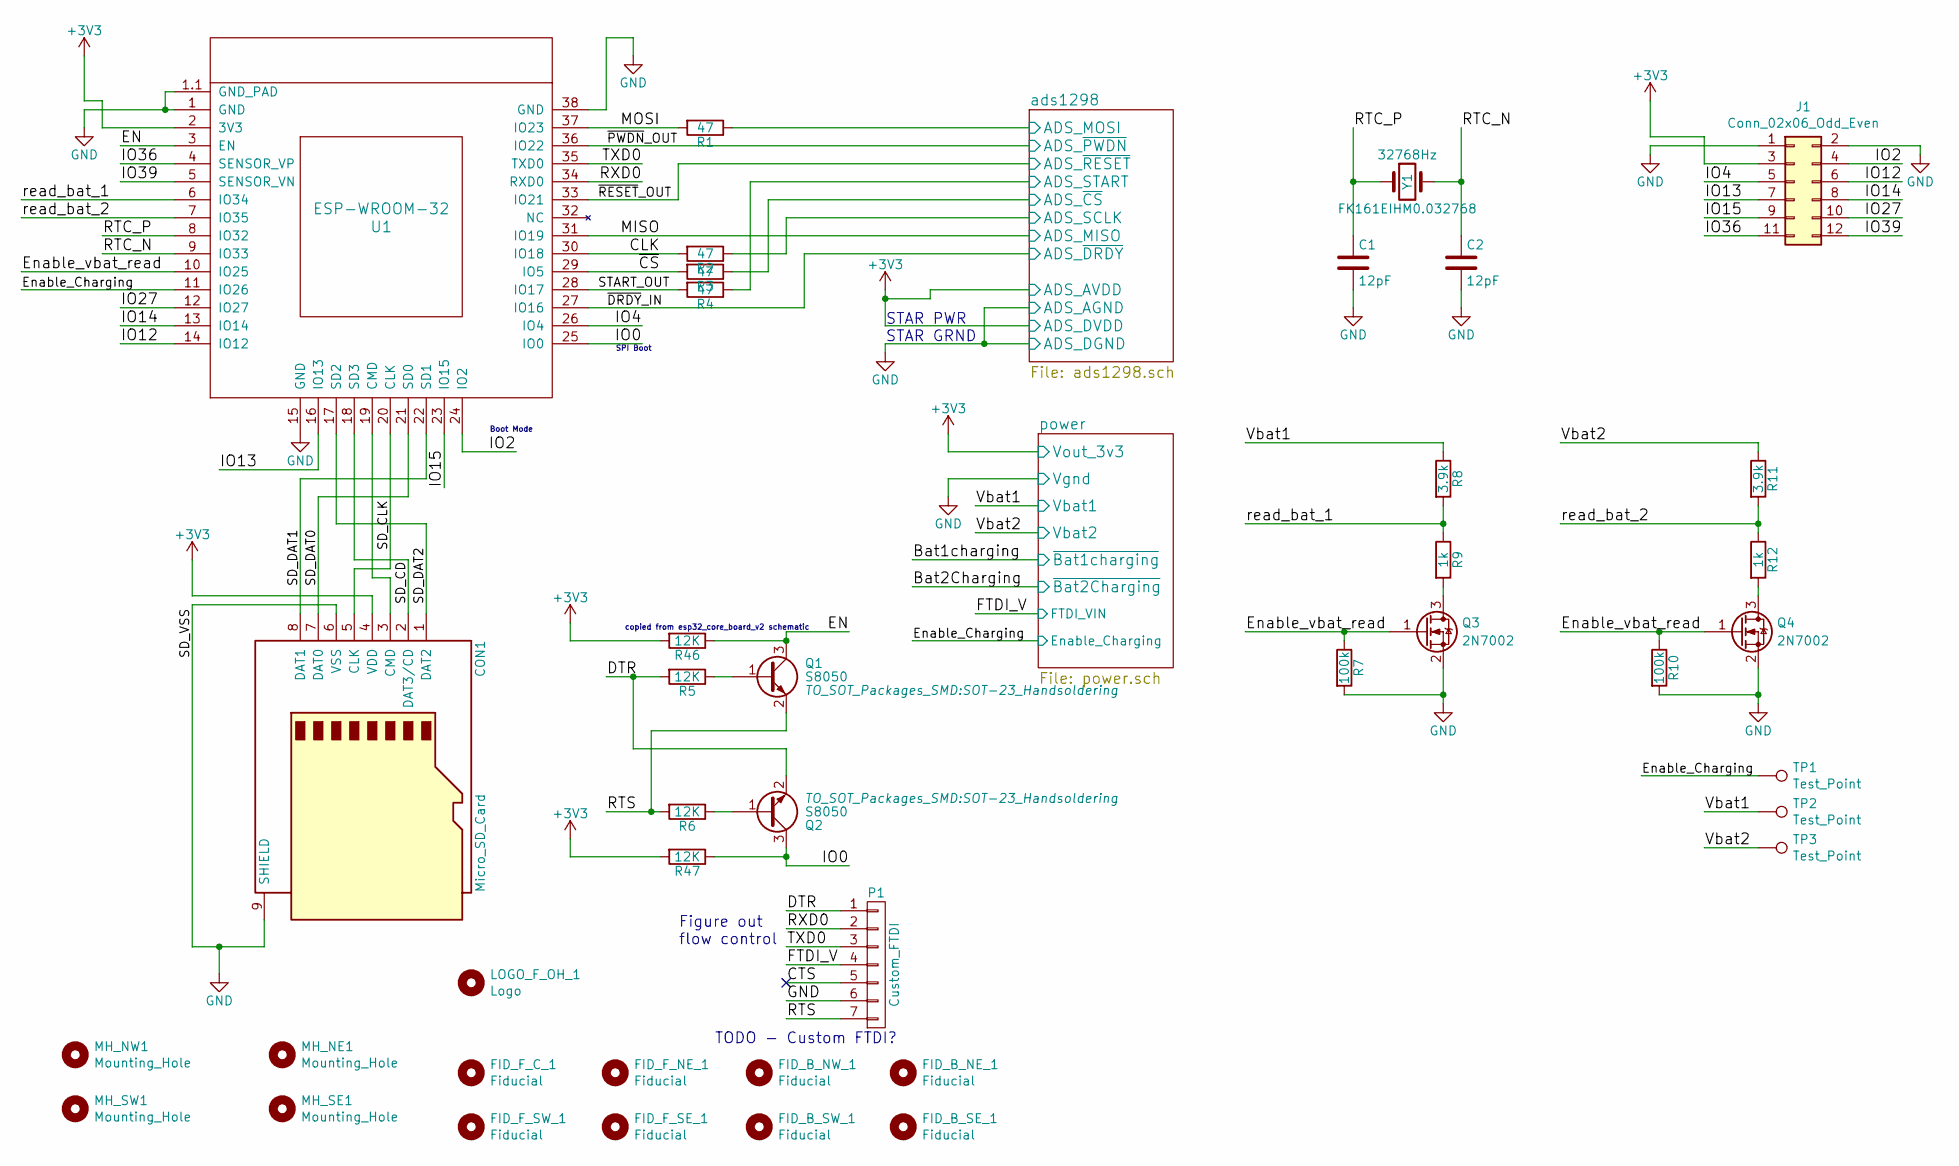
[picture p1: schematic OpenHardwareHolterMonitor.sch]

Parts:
C1, C2: 12pF; C_0603_HandSoldering
CON1: Micro_SD_Card; MicroSd_Wurth_693072010801
FID_B_NE_1: Fiducial; Fiducial_1mm_Dia_2.54mm_Outer_CopperTop
FID_B_NW_1: Fiducial; Fiducial_1mm_Dia_2.54mm_Outer_CopperTop
FID_B_SE_1: Fiducial; Fiducial_1mm_Dia_2.54mm_Outer_CopperTop
FID_B_SW_1: Fiducial; Fiducial_1mm_Dia_2.54mm_Outer_CopperTop
FID_F_C_1: Fiducial; Fiducial_1mm_Dia_2.54mm_Outer_CopperTop
FID_F_NE_1: Fiducial; Fiducial_1mm_Dia_2.54mm_Outer_CopperTop
FID_F_SE_1: Fiducial; Fiducial_1mm_Dia_2.54mm_Outer_CopperTop
FID_F_SW_1: Fiducial; Fiducial_1mm_Dia_2.54mm_Outer_CopperTop
J1: Conn_02x06_Odd_Even; Pin_Header_Straight_2x06_Pitch1.27mm
LOGO_F_OH_1: Logo; OSHW-Logo2_9.8x8mm_SilkScreen
MH_NE1: Mounting_Hole; MountingHole_2.2mm_M2_ISO7380
MH_NW1: Mounting_Hole; MountingHole_2.2mm_M2_ISO7380
MH_SE1: Mounting_Hole; MountingHole_2.2mm_M2_ISO7380
MH_SW1: Mounting_Hole; MountingHole_2.2mm_M2_ISO7380
P1: Custom_FTDI; Pin_Header_Straight_1x07_Pitch2.54mm
Q1, Q2: S8050; SOT-23_Handsoldering
Q3, Q4: 2N7002; SOT-23_Handsoldering
R1, R2, R3, R4: 47; R_0603_1608Metric_Pad1.05x0.95mm_HandSolder
R5, R6, R46, R47: 12K; R_0603_1608Metric_Pad1.05x0.95mm_HandSolder
R7, R10: 100k; R_0603_1608Metric_Pad1.05x0.95mm_HandSolder
R8, R11: 3.9k; R_0603_1608Metric_Pad1.05x0.95mm_HandSolder
R9, R12: 1k; R_0603_1608Metric_Pad1.05x0.95mm_HandSolder
TP1, TP2, TP3: Test_Point; Measurement_Point_Square-SMD-Pad_Small
U1: ESP-WROOM-32; MODULE_ESP-WROOM-32
Y1: 32768Hz; K161

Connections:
+3V3: CON1.4 (VDD), J1.3, R46.2, R47.2, U1.2 (3V3); also elsewhere on the board
/CLK: R2.2, U1.30 (IO18)
/CTS: P1.5
/DTR: P1.1, Q2.2 (E), R5.2
/EN: Q1.3 (C), R46.1, U1.3 (EN)
/Enable_Charging: TP1.1, U1.11 (IO26); also elsewhere on the board
/Enable_vbat_read: Q3.1 (G), Q4.1 (G), R7.1, R10.1, U1.10 (IO25)
/FTDI_V: P1.4; also elsewhere on the board
/IO0: Q2.3 (C), R47.1, U1.25 (IO0)
/IO2: J1.4, U1.24 (IO2)
/IO4: J1.5, U1.26 (IO4)
/IO12: J1.6, U1.14 (IO12)
/IO13: J1.7, U1.16 (IO13)
/IO14: J1.8, U1.13 (IO14)
/IO15: J1.9, U1.23 (IO15)
/IO27: J1.10, U1.12 (IO27)
/IO36: J1.11, U1.4 (SENSOR_VP)
/IO39: J1.12, U1.5 (SENSOR_VN)
/MISO: U1.31 (IO19); also elsewhere on the board
/MOSI: R1.2, U1.37 (IO23)
/RTC_N: C2.1, U1.9 (IO33), Y1.2
/RTC_P: C1.1, U1.8 (IO32), Y1.1
/RTS: P1.7, Q1.2 (E), R6.2
/RXD0: P1.2, U1.34 (RXD0)
/SD_CD: CON1.2 (DAT3/CD), U1.18 (SD3)
/SD_CLK: CON1.5 (CLK), U1.20 (CLK)
/SD_DAT0: CON1.7 (DAT0), U1.21 (SD0)
/SD_DAT1: CON1.8 (DAT1), U1.22 (SD1)
/SD_DAT2: CON1.1 (DAT2), U1.17 (SD2)
/START_OUT: R4.2, U1.28 (IO17)
/TXD0: P1.3, U1.35 (TXD0)
/Vbat1: R8.1, TP2.1; also elsewhere on the board
/Vbat2: R11.1, TP3.1; also elsewhere on the board
/ads1298/ADS_MOSI: R1.1; also elsewhere on the board
/ads1298/ADS_SCLK: R2.1; also elsewhere on the board
/ads1298/ADS_START: R4.1; also elsewhere on the board
/ads1298/ADS_~CS~: R3.1; also elsewhere on the board
/read_bat_1: R8.2, R9.1, U1.6 (IO34)
/read_bat_2: R11.2, R12.1, U1.7 (IO35)
/~CS~: R3.2, U1.29 (IO5)
/~DRDY~_IN: U1.27 (IO16); also elsewhere on the board
/~PWDN~_OUT: U1.36 (IO22); also elsewhere on the board
/~RESET~_OUT: U1.33 (IO21); also elsewhere on the board
GND: C1.2, C2.2, CON1.6 (VSS), CON1.9 (SHIELD), J1.1, J1.2, P1.6, Q3.2 (S), Q4.2 (S), R7.2, R10.2, U1.1 (GND), U1.1.1 (GND_PAD), U1.15 (GND), U1.38 (GND); also elsewhere on the board
unnamed: CON1.3 (CMD), U1.19 (CMD)
unnamed: Q1.1 (B), R5.1
unnamed: Q2.1 (B), R6.1
unnamed: Q3.3 (D), R9.2
unnamed: Q4.3 (D), R12.2

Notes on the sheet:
copied from esp32_core_board_v2 schematic
Figure out flow control
Boot Mode
SPI Boot
STAR PWR STAR GRND
TODO - Custom FTDI?

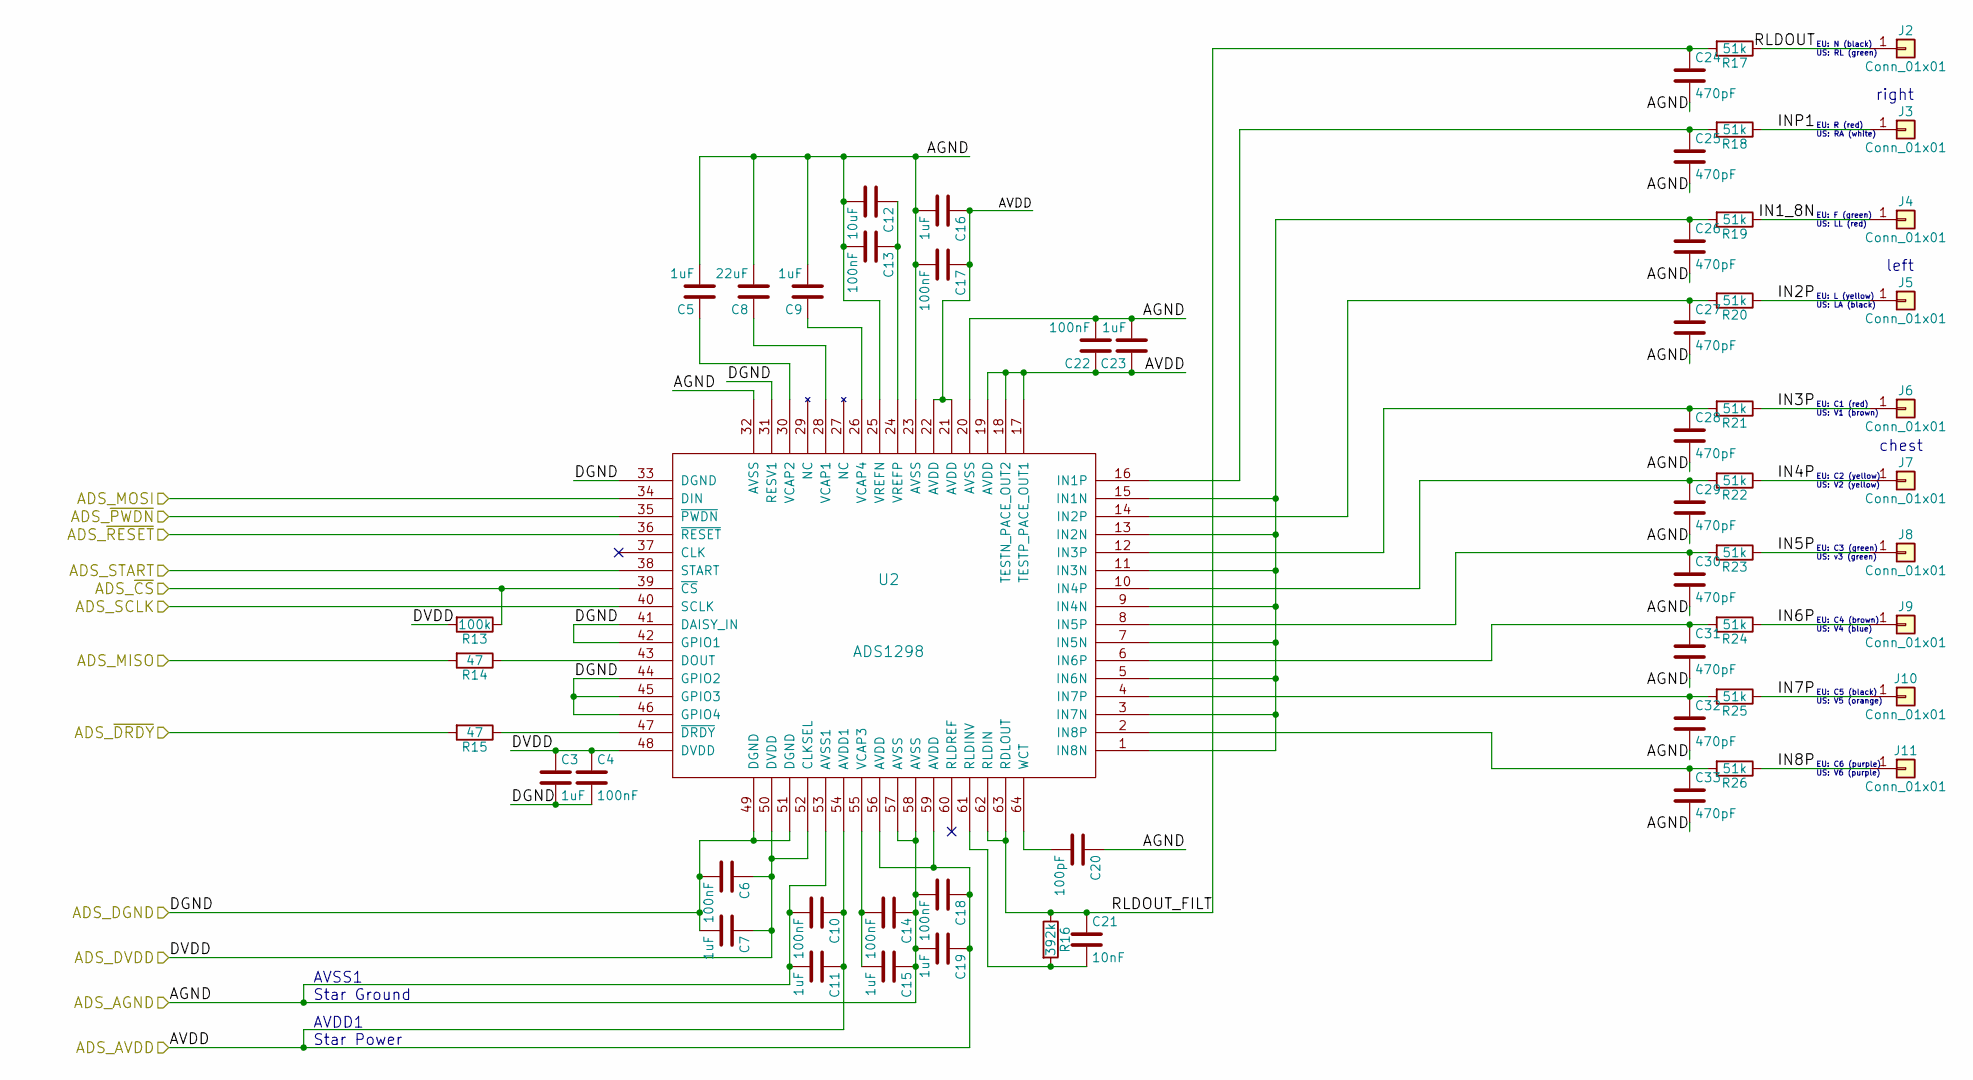
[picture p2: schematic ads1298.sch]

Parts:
C3, C5, C7, C9, C11, C15, C16, C19, C23: 1uF; C_0603_HandSoldering
C4, C6, C10, C13, C14, C17, C18, C22: 100nF; C_0603_HandSoldering
C8: 22uF; C_0805_HandSoldering
C12: 10uF; C_0805_HandSoldering
C20: 100pF; C_0603_HandSoldering
C21: 10nF; C_0603_HandSoldering
C24, C25, C26, C27, C28, C29, C30, C31, C32, C33: 470pF; C_0603_HandSoldering
J2, J3, J4, J5, J6, J7, J8, J9, J10, J11: Conn_01x01; PlasticsOne_41828
R13: 100k; R_0603_1608Metric_Pad1.05x0.95mm_HandSolder
R14, R15: 47; R_0603_1608Metric_Pad1.05x0.95mm_HandSolder
R16: 392k; R_0603_1608Metric_Pad1.05x0.95mm_HandSolder
R17, R18, R19, R20, R21, R22, R23, R24, R25, R26: 51k; R_Axial_Power_L20.0mm_W6.4mm_P25.40mm
U2: ADS1298; LQFP-64_10x10mm_Pitch0.5mm

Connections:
+3V3: C3.1, C4.1, C6.1, C7.1, C10.1, C11.1, C16.1, C17.1, C18.1, C19.1, C22.1, C23.1, R13.2, U2.17 (TESTP_PACE_OUT1), U2.18 (TESTN_PACE_OUT2), U2.19 (AVDD), U2.21 (AVDD), U2.22 (AVDD), U2.48 (DVDD), U2.50 (DVDD), U2.52 (CLKSEL), U2.54 (AVDD1), U2.56 (AVDD), U2.59 (AVDD); also elsewhere on the board
/MISO: R14.2; also elsewhere on the board
/ads1298/ADS_MOSI: U2.34 (DIN); also elsewhere on the board
/ads1298/ADS_SCLK: U2.40 (SCLK); also elsewhere on the board
/ads1298/ADS_START: U2.38 (START); also elsewhere on the board
/ads1298/ADS_~CS~: R13.1, U2.39 (~CS~); also elsewhere on the board
/ads1298/IN1_8N: J4.1, R19.1
/ads1298/IN2P: J5.1, R20.1
/ads1298/IN3P: J6.1, R21.1
/ads1298/IN4P: J7.1, R22.1
/ads1298/IN5P: J8.1, R23.1
/ads1298/IN6P: J9.1, R24.1
/ads1298/IN7P: J10.1, R25.1
/ads1298/IN8P: J11.1, R26.1
/ads1298/INP1: J3.1, R18.1
/ads1298/RLDOUT: J2.1, R17.1
/ads1298/RLDOUT_FILT: C21.1, C24.1, R16.1, R17.2, U2.62 (RLDIN), U2.63 (RDLOUT)
/~DRDY~_IN: R15.2; also elsewhere on the board
/~PWDN~_OUT: U2.35 (~PWDN~); also elsewhere on the board
/~RESET~_OUT: U2.36 (~RESET~); also elsewhere on the board
GND: C3.2, C4.2, C5.2, C6.2, C7.2, C8.2, C9.2, C10.2, C11.2, C12.2, C13.2, C14.1, C15.1, C16.2, C17.2, C18.2, C19.2, C20.1, C22.2, C23.2, C24.2, C25.2, C26.2, C27.2, C28.2, C29.2, C30.2, C31.2, C32.2, C33.2, U2.20 (AVSS), U2.23 (AVSS), U2.25 (VREFN), U2.31 (RESV1), U2.32 (AVSS), U2.33 (DGND), U2.41 (DAISY_IN), U2.42 (GPIO1), U2.44 (GPIO2), U2.45 (GPIO3), U2.46 (GPIO4), U2.49 (DGND), U2.51 (DGND), U2.53 (AVSS1), U2.57 (AVSS), U2.58 (AVSS); also elsewhere on the board
unnamed: C5.1, U2.30 (VCAP2)
unnamed: C8.1, U2.28 (VCAP1)
unnamed: C9.1, U2.26 (VCAP4)
unnamed: C12.1, C13.1, U2.24 (VREFP)
unnamed: C14.2, C15.2, U2.55 (VCAP3)
unnamed: C20.2, U2.64 (WCT)
unnamed: C21.2, R16.2, U2.61 (RLDINV)
unnamed: C25.1, R18.2, U2.16 (IN1P)
unnamed: C26.1, R19.2, U2.1 (IN8N), U2.3 (IN7N), U2.5 (IN6N), U2.7 (IN5N), U2.9 (IN4N), U2.11 (IN3N), U2.13 (IN2N), U2.15 (IN1N)
unnamed: C27.1, R20.2, U2.14 (IN2P)
unnamed: C28.1, R21.2, U2.12 (IN3P)
unnamed: C29.1, R22.2, U2.10 (IN4P)
unnamed: C30.1, R23.2, U2.8 (IN5P)
unnamed: C31.1, R24.2, U2.6 (IN6P)
unnamed: C32.1, R25.2, U2.4 (IN7P)
unnamed: C33.1, R26.2, U2.2 (IN8P)
unnamed: R14.1, U2.43 (DOUT)
unnamed: R15.1, U2.47 (~DRDY~)

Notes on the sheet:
AVSS1 Star Ground
AVDD1 Star Power
EU: R (red) US: RA (white)
EU: N (black) US: RL (green)
EU: F (green) US: LL (red)
EU: L (yellow) US: LA (black)
EU: C1 (red) US: V1 (brown)
EU: C2 (yellow) US: V2 (yellow)
EU: C3 (green) US: v3 (green)
EU: C4 (brown) US: V4 (blue)
EU: C5 (black) US: V5 (orange)
EU: C6 (purple) US: V6 (purple)
right
left
chest

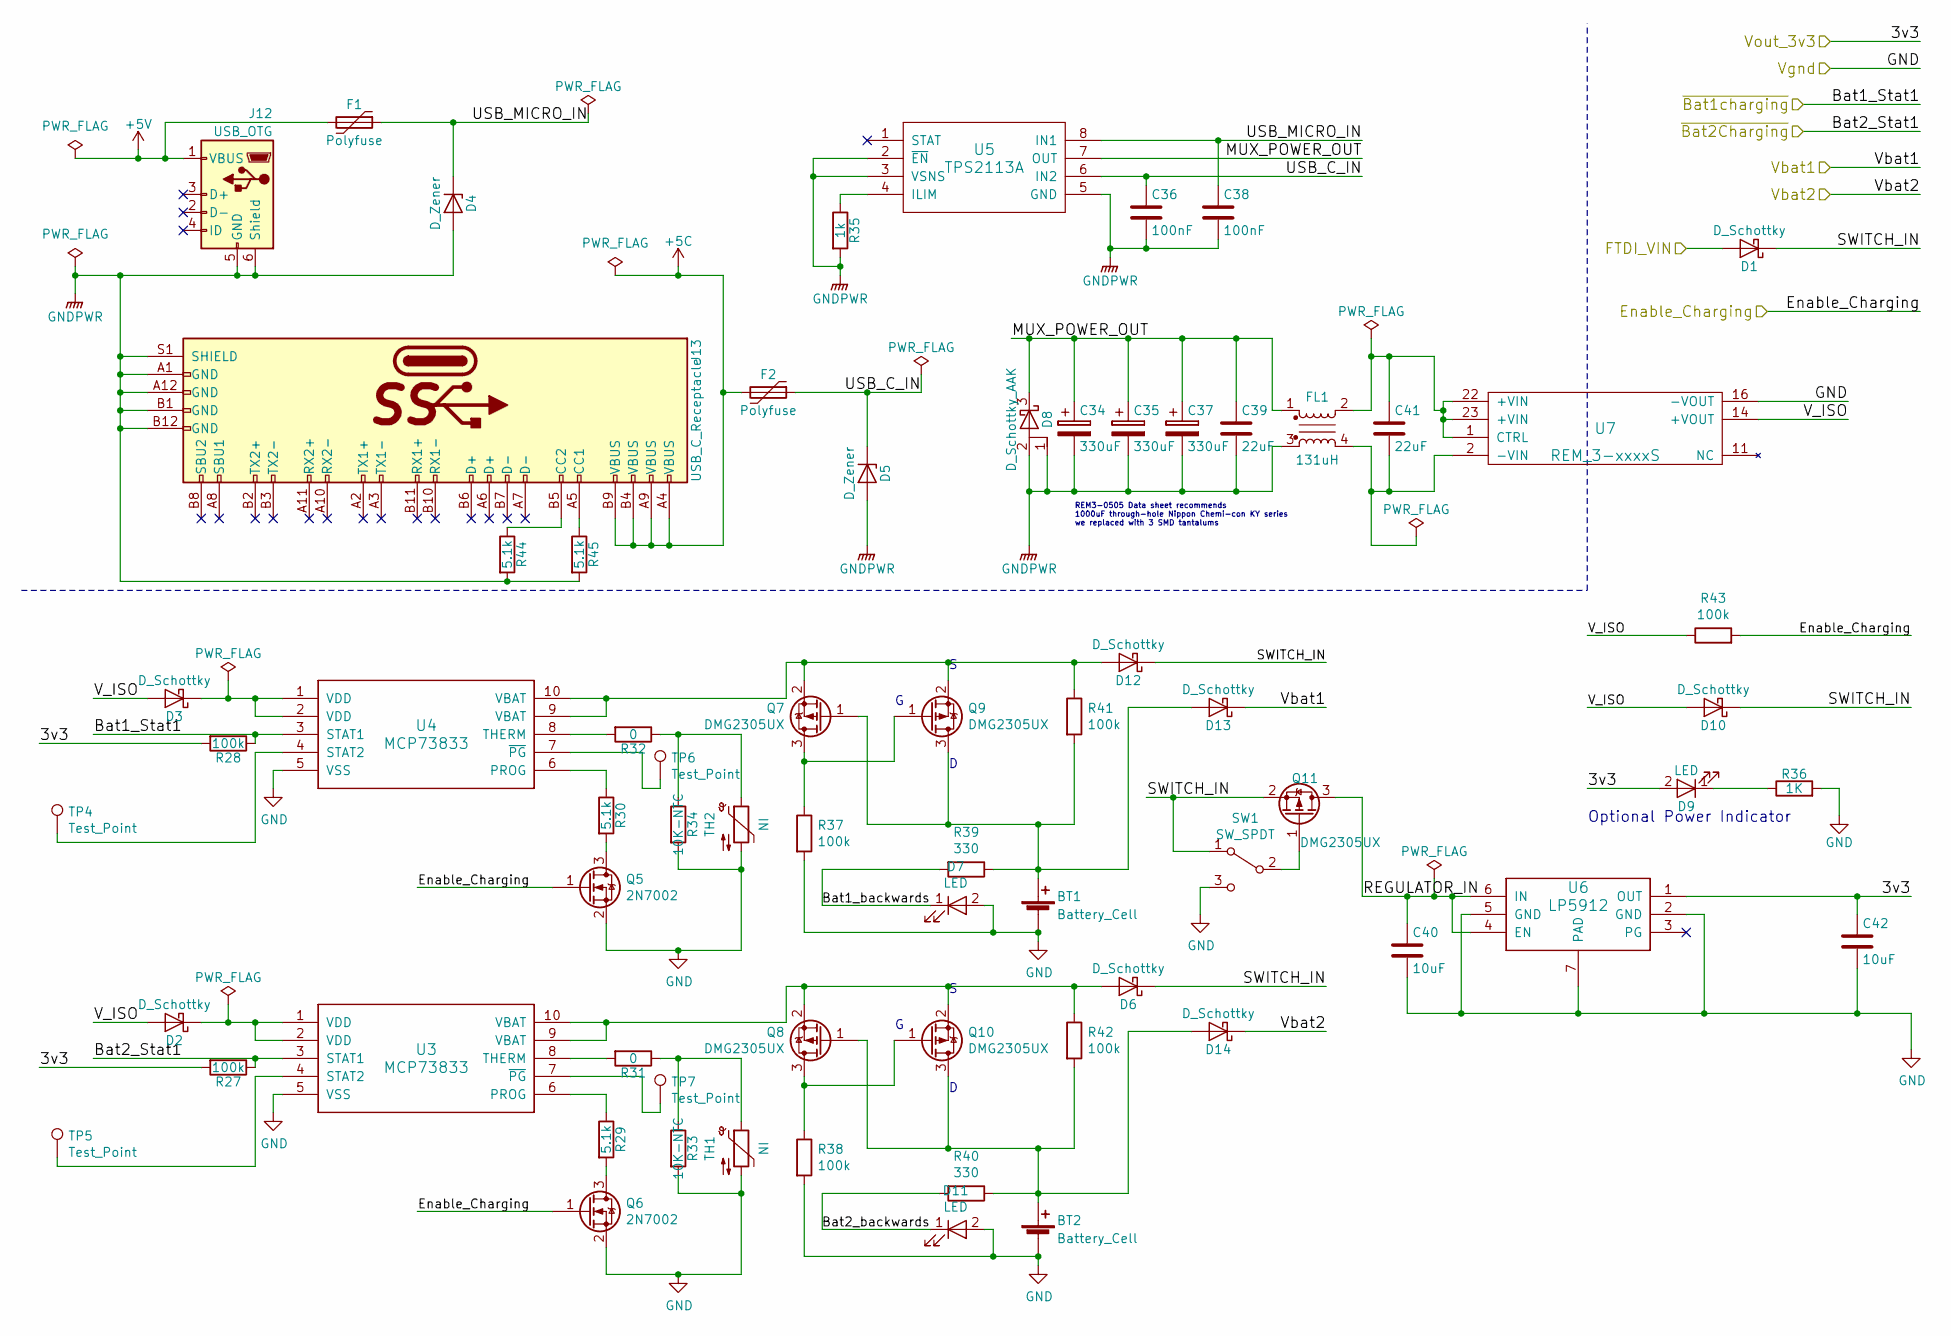
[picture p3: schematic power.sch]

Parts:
BT1, BT2: Battery_Cell; Keystone1043
C34, C35, C37: 330uF; CP_Tantalum_Case-E_EIA-7260-38_Hand
C36, C38: 100nF; C_0603_HandSoldering
C39, C41: 22uF; C_0805_HandSoldering
C40, C42: 10uF; C_0805_HandSoldering
D1, D2, D3, D6, D10, D12, D13, D14: D_Schottky; D_SOD-323_HandSoldering
D4, D5: D_Zener; D_SMB_Handsoldering
D7, D9, D11: LED; LED_0603_HandSoldering
D8: D_Schottky_AAK; TO-277A
F1, F2: Polyfuse; R_1812_HandSoldering
FL1: 131uH; CMS1
J12: USB_OTG; USB_Micro-B_Wuerth-629105150521_CircularHoles
J13: USB_C_Receptacle; USB_C_Receptacle_Amphenol_12401610E4-2A_CircularHoles
Q5, Q6: 2N7002; SOT-23_Handsoldering
Q7, Q8, Q9, Q10, Q11: DMG2305UX; SOT-23_Handsoldering
R27, R28, R37, R38, R41, R42, R43: 100k; R_0603_1608Metric_Pad1.05x0.95mm_HandSolder
R29, R30, R44, R45: 5.1k; R_0603_1608Metric_Pad1.05x0.95mm_HandSolder
R31, R32: 0; R_0603_1608Metric_Pad1.05x0.95mm_HandSolder
R33, R34: 10K-NTC; R_0603_1608Metric_Pad1.05x0.95mm_HandSolder
R35: 1k; R_0603_1608Metric_Pad1.05x0.95mm_HandSolder
R36: 1K; R_0603_1608Metric_Pad1.05x0.95mm_HandSolder
R39, R40: 330; R_0603_1608Metric_Pad1.05x0.95mm_HandSolder
SW1: SW_SPDT; SW_SPDT_CK-JS102011SAQN
TH1, TH2: NI; CP_Radial_D4.0mm_P1.50mm
TP4, TP5, TP6, TP7: Test_Point; Measurement_Point_Square-SMD-Pad_Small
U3, U4: MCP73833; MSOP-10_3x3mm_Pitch0.5mm
U5: TPS2113A; TSSOP-8_4.4x3mm_Pitch0.65mm
U6: LP5912; WSON-6_2x2mm_Pitch0.65mm
U7: REM_3-xxxxS; REM3

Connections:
+3V3: C42.1, D9.2 (A), R27.2, R28.2, U6.1 (OUT); also elsewhere on the board
+5C: F2.2, J13.A4 (VBUS), J13.A9 (VBUS), J13.B4 (VBUS), J13.B9 (VBUS)
+5V: F1.2, J12.1 (VBUS)
/Bat1charging: R28.1, U4.3 (STAT1)
/Bat2Charging: R27.1, U3.3 (STAT1)
/Enable_Charging: Q5.1 (G), Q6.1 (G), R43.2; also elsewhere on the board
/FTDI_V: D1.2 (A); also elsewhere on the board
/Vbat1: D13.1 (K); also elsewhere on the board
/Vbat2: D14.1 (K); also elsewhere on the board
/power/Bat1_backwards: D7.1 (K), R39.2
/power/Bat2_backwards: D11.1 (K), R40.2
/power/MUX_POWER_OUT: C34.1, C35.1, C37.1, C39.1, D8.3 (K), FL1.1, U5.7 (OUT)
/power/REGULATOR_IN: C40.1, Q11.3 (D), U6.4 (EN), U6.6 (IN)
/power/SWITCH_IN: D1.1 (K), D6.1 (K), D10.1 (K), D12.1 (K), Q11.2 (S), SW1.1 (A)
/power/USB_C_IN: C36.1, D5.1 (K), F2.1, U5.6 (IN2)
/power/USB_MICRO_IN: C38.1, D4.1 (K), F1.1, U5.8 (IN1)
/power/V_ISO: D2.2 (A), D3.2 (A), D10.2 (A), R43.1, U7.14 (+VOUT)
GND: BT1.2 (-), BT2.2 (-), C40.2, C42.2, D7.2 (A), D11.2 (A), Q5.2 (S), Q6.2 (S), R33.2, R34.2, R36.2, R37.2, R38.2, SW1.3 (C), TH1.2, TH2.2, U3.5 (VSS), U4.5 (VSS), U6.2 (GND), U6.5 (GND), U6.7 (PAD), U7.16 (-VOUT); also elsewhere on the board
GNDPWR: C34.2, C35.2, C36.2, C37.2, C38.2, C39.2, D4.2 (A), D5.2 (A), D8.1 (A), D8.2 (A), FL1.3, J12.5 (GND), J12.6 (Shield), J13.A1 (GND), J13.A12 (GND), J13.B1 (GND), J13.B12 (GND), J13.S1 (SHIELD), R35.2, R44.2, R45.2, U5.2 (~EN~), U5.3 (VSNS), U5.5 (GND)
unnamed: BT1.1 (+), D13.2 (A), Q7.1 (G), Q9.3 (D), R39.1, R41.2
unnamed: BT2.1 (+), D14.2 (A), Q8.1 (G), Q10.3 (D), R40.1, R42.2
unnamed: C41.1, FL1.2, U7.1 (CTRL), U7.22 (+VIN), U7.23 (+VIN)
unnamed: C41.2, FL1.4, U7.2 (-VIN)
unnamed: D2.1 (K), U3.1 (VDD), U3.2 (VDD)
unnamed: D3.1 (K), U4.1 (VDD), U4.2 (VDD)
unnamed: D6.2 (A), Q8.2 (S), Q10.2 (S), R42.1, U3.9 (VBAT), U3.10 (VBAT)
unnamed: D9.1 (K), R36.1
unnamed: D12.2 (A), Q7.2 (S), Q9.2 (S), R41.1, U4.9 (VBAT), U4.10 (VBAT)
unnamed: J13.A5 (CC1), R45.1
unnamed: J13.B5 (CC2), R44.1
unnamed: Q5.3 (D), R30.2
unnamed: Q6.3 (D), R29.2
unnamed: Q7.3 (D), Q9.1 (G), R37.1
unnamed: Q8.3 (D), Q10.1 (G), R38.1
unnamed: Q11.1 (G), SW1.2 (B)
unnamed: R29.1, U3.6 (PROG)
unnamed: R30.1, U4.6 (PROG)
unnamed: R31.1, R33.1, TH1.1
unnamed: R31.2, U3.8 (THERM)
unnamed: R32.1, R34.1, TH2.1
unnamed: R32.2, U4.8 (THERM)
unnamed: R35.1, U5.4 (ILIM)
unnamed: TP4.1, U4.4 (STAT2)
unnamed: TP5.1, U3.4 (STAT2)
unnamed: TP6.1, U4.7 (~PG~)
unnamed: TP7.1, U3.7 (~PG~)

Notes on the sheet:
REM3-0505 Data sheet recommends 1000uF through-hole Nippon Chemi-con KY series we replaced with 3 SMD tantalums
Optional Power Indicator

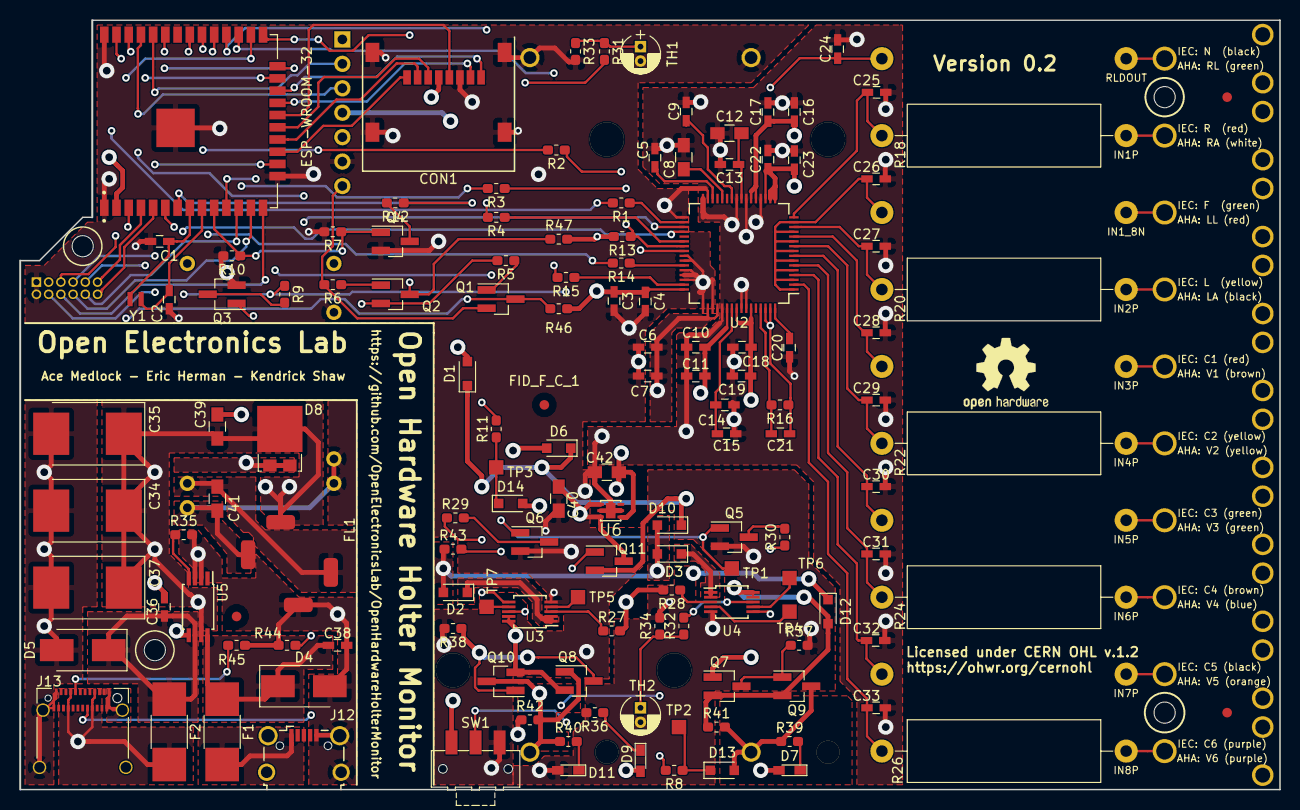
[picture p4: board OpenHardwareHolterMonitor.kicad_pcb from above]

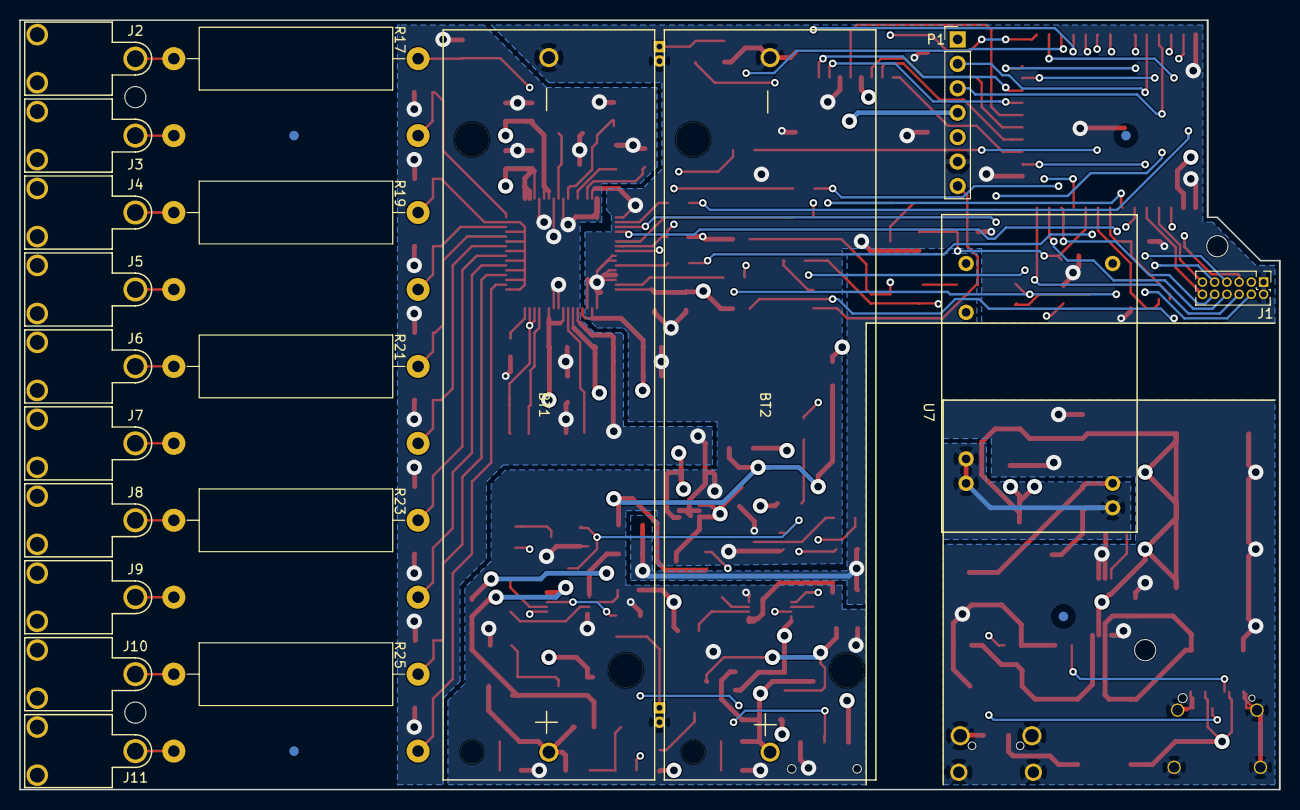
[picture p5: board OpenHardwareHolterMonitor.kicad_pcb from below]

Board: 6 copper layers, 131.0 x 80.0 mm, 165 parts (24 on the bottom side), 117 nets.

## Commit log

2017-12-02 ESP32 for kicad
    data sheet at:
    https://cdn.sparkfun.com/datasheets/IoT/esp32_datasheet_en.pdf
2017-12-02 checkpoint schematic with ESP32
    [OpenHardwareHolterMonitor.kicad_pcb, OpenHardwareHolterMonitor.sch]
2017-12-02 ESP32 add ground pad as pin 49
    version 2 of the datasheet:
    https://www.espressif.com/sites/default/files/documentation/esp32_datasheet_en.pdf
2017-12-09 checkpoint with SD card and ADS sketched-in
    [OpenHardwareHolterMonitor.sch]
2017-12-09 sketch in some connections
    [OpenHardwareHolterMonitor.sch]
2017-12-09 swap-in 1298
    [OpenHardwareHolterMonitor.sch]
2017-12-09 fix lib location
    [OpenHardwareHolterMonitor.sch]
2017-12-25 extract ADS into separate sheet
    [OpenHardwareHolterMonitor.sch, ads1298.sch]
2017-12-25 add power decoupling caps to ADS
    [ads1298.sch]
2017-12-25 ads schematic cleanup and add source termination
    [ads1298.sch]
2018-01-06 add anti-aliasing filters
    [OpenHardwareHolterMonitor.sch, ads1298.sch]
2018-01-06 some power notes
2018-01-13 power notes
2018-01-13 voltage drop notes
2018-01-27 simplify anti-aliasing filter
    new low-pass filter cuts off at about 6.6KHz
    >>> 1/(2 * math.pi * 51e3 * 470e-12)
    6639.755656733221
    [ads1298.sch]
2018-01-27 sketch-in a battery
    [OpenHardwareHolterMonitor.sch, ads1298.sch, power.sch]
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2018-02-10 sketch-in thermister to power sheet
    [power.sch]
2018-03-17 added micro-USB and isolated power
    [OpenHardwareHolterMonitor.sch, ads1298.sch, power.sch]
2018-03-24 schematic first draft
    [OpenHardwareHolterMonitor.sch, ads1298.sch, power.sch]
2018-03-24 add vbat to header, and optional power LED
    [OpenHardwareHolterMonitor.sch, power.sch]
2018-04-15 sketch-in USB C power option, TODO: add power muxer
    [power.sch]
2018-06-02 multiplex power-in
    [OpenHardwareHolterMonitor.sch, ads1298.sch, power.sch]
2018-06-02 fix rules-check issues
    [OpenHardwareHolterMonitor.sch, ads1298.sch, power.sch]
2018-06-02 assign some footprints
    [OpenHardwareHolterMonitor.sch, ads1298.sch, power.sch]
2018-06-09 kicad from git repo
    https://git.launchpad.net/kicad
    8444b1b6176249060196c22cf0d5027d92f93854
    https://git.launchpad.net/kicad-library
    bb856328eef2676d859dfa179a6c078922a42274
    [OpenHardwareHolterMonitor-2018-06-09-13-56-16.sch, OpenHardwareHolterMonitor.sch, ads1298-2018-06-09-13-56-16.sch, ads1298.sch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]
2018-06-09 add some footprints
    [ads1298.sch, power.sch]
2018-06-16 more footprints
    [ads1298.sch, power.sch]
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2018-06-16 more footprint usage
    [OpenHardwareHolterMonitor.sch, power.sch]
2018-06-16 finish footprints
    [OpenHardwareHolterMonitor.sch, power.sch]
2018-09-15 checkpoint initial pcb file
    [OpenHardwareHolterMonitor.kicad_pcb, power.sch]
2018-09-15 checkpoint 2 pcb file
    [OpenHardwareHolterMonitor.kicad_pcb]
2018-09-15 checkpoint 3 pcb file
    [OpenHardwareHolterMonitor.kicad_pcb, power.sch]
2018-10-13 wire-up power/gnd, caps to ads1298
    [OpenHardwareHolterMonitor.kicad_pcb, ads1298.sch, power.sch]
2018-10-20 checkpoint; non-isolated layout
    [OpenHardwareHolterMonitor.kicad_pcb, OpenHardwareHolterMonitor.sch, power.sch]
2018-10-20 checkpoint layout
    [OpenHardwareHolterMonitor.kicad_pcb]
2018-10-20 next up, isolated power layout
    [OpenHardwareHolterMonitor.kicad_pcb]
2018-11-03 add battery reversal protection to schematic
    [OpenHardwareHolterMonitor.kicad_pcb, OpenHardwareHolterMonitor.sch, power.sch]
2018-11-03 un-isolated power layout
    [OpenHardwareHolterMonitor.kicad_pcb]
2018-11-03 board layout checkpoint
    [OpenHardwareHolterMonitor.kicad_pcb, OpenHardwareHolterMonitor.sch, power.sch]
2018-11-03 checkpoint PCB
    [OpenHardwareHolterMonitor.kicad_pcb]
2018-11-10 charger layout
    [OpenHardwareHolterMonitor.kicad_pcb, power.sch]
2018-11-24 initial hook-up of isolated side
    [OpenHardwareHolterMonitor.kicad_pcb]
2018-11-24 non-isolated hook-up
    [OpenHardwareHolterMonitor.kicad_pcb]
2018-11-24 pre-notch checkpoint
    [OpenHardwareHolterMonitor.kicad_pcb]
2018-11-24 ready for holes and zones
    [OpenHardwareHolterMonitor.kicad_pcb]
2018-12-01 checkpoint for kicad upgrade
    [OpenHardwareHolterMonitor.kicad_pcb]
2018-12-01 switch to 6 layer board
    [OpenHardwareHolterMonitor.kicad_pcb]
2018-12-01 power lines 0.5mm
    [OpenHardwareHolterMonitor.kicad_pcb]
2018-12-01 isolated ground planes
    [OpenHardwareHolterMonitor.kicad_pcb]
2018-12-08 widen power tracks
    [OpenHardwareHolterMonitor.kicad_pcb]
2018-12-08 finishing up zones
    [OpenHardwareHolterMonitor.kicad_pcb]
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2018-12-15 DRC passes (with some missing courtyard warnings)
    [OpenHardwareHolterMonitor.kicad_pcb]
2018-12-15 esp-wroom footprint update
    [OpenHardwareHolterMonitor.kicad_pcb, OpenHardwareHolterMonitor.sch]
2018-12-15 add basic courtyards to footprints
    [OpenHardwareHolterMonitor.kicad_pcb]
2018-12-17 add debug labels
    [OpenHardwareHolterMonitor.kicad_pcb]
2018-12-22 align physical items with schematic
    [OpenHardwareHolterMonitor.kicad_pcb, OpenHardwareHolterMonitor.sch, power.sch]
2018-12-22 add the first few part numbers
    [OpenHardwareHolterMonitor.sch, ads1298.sch, power.sch]
2019-01-05 add fiducial marks
    [OpenHardwareHolterMonitor.kicad_pcb]
2019-01-05 Add logos and text to silkscreen layer
    [OpenHardwareHolterMonitor.kicad_pcb]
2019-01-05 add gerber files
    [OpenHardwareHolterMonitor-B.Cu.horiz.gbr, OpenHardwareHolterMonitor-B.Mask.gbr, OpenHardwareHolterMonitor-B.Paste.gbr, OpenHardwareHolterMonitor-B.SilkS.gbr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]
2019-01-12 continue assigning part numbers for BOM
    [OpenHardwareHolterMonitor.sch, ads1298.sch, power.sch]
2019-01-19 replace switch and rework pcb
    [OpenHardwareHolterMonitor.kicad_pcb, power.sch]
2019-01-19 flipped alternating resistors to increase clearance between
    [OpenHardwareHolterMonitor.kicad_pcb]
2019-01-19 more parts of the BOM
    [OpenHardwareHolterMonitor.kicad_pcb, power.sch]
2019-01-26 fix some part typos
    [ads1298.sch, power.sch]
2019-01-26 someone set us up the BoM
    [OpenHardwareHolterMonitor.sch, ads1298.sch, power.sch]
2019-02-09 checked BoM
    [OpenHardwareHolterMonitor.sch, ads1298.sch, power.sch]
2019-02-09 eliminate old notes from schematic or move to notes.txt
    [ads1298.sch, power.sch]
2019-02-09 fix-up pcb with new footprints
    [OpenHardwareHolterMonitor.kicad_pcb]
2019-03-09 checkpoint silk layout
    [OpenHardwareHolterMonitor.kicad_pcb]
2019-03-09 finish board v0.1
    [OpenHardwareHolterMonitor.kicad_pcb]
2019-03-09 generate gerbers
    [OpenHardwareHolterMonitor-B.Cu.horiz.gbr, OpenHardwareHolterMonitor-B.Mask.gbr, OpenHardwareHolterMonitor-B.Paste.gbr, OpenHardwareHolterMonitor-B.SilkS.gbr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]
2019-03-09 generated BOM
    [OpenHardwareHolterMonitor_bom_.csv]
2019-03-09 add a goldphoenix BoM without touchproof connectors
    [OpenHardwareHolterMonitor_bom_goldphoenix.csv]
2019-03-16 rework BoM via digikey for goldphoenix
    [digikey_bom_2.xlsx]
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2019-06-15 note options for board errors
2019-06-22 fix schematic to use standard transistor pin numbers
    [OpenHardwareHolterMonitor.sch, power.sch]
2019-06-22 switch to consistent SOT-23 footprint
    [OpenHardwareHolterMonitor.sch, power.sch]
2019-06-22 fixed pcb for transistor pinouts
    [OpenHardwareHolterMonitor.kicad_pcb, power.sch]
2019-07-13 re-add Fiducial marks
    [OpenHardwareHolterMonitor.kicad_pcb]
2019-07-13 re-add open hardware logo
    [OpenHardwareHolterMonitor.kicad_pcb]
2019-07-13 Align Fiducials and Logo on schematic and PCB
    [OpenHardwareHolterMonitor.kicad_pcb, OpenHardwareHolterMonitor.sch, ads1298.sch, power.sch]
2019-07-13 refill & DRC
    [OpenHardwareHolterMonitor.kicad_pcb]
2019-07-13 fix lables R17-R26
    [OpenHardwareHolterMonitor.kicad_pcb]
2019-07-13 align back copper power zone with other layers
    [OpenHardwareHolterMonitor.kicad_pcb]
2019-07-13 fix CMS1 footprint
    [OpenHardwareHolterMonitor.kicad_pcb]
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2019-08-24 starting on case design
    [OpenHardwareHolterMonitor_case.scad]
2019-08-31 case: finish board keepout model
    [OpenHardwareHolterMonitor_case.scad]
2019-08-31 refactoring of case OpenSCAD code
    [OpenHardwareHolterMonitor_case.scad]
2019-08-31 initial minimal case design
    [OpenHardwareHolterMonitor_case.scad]
2019-08-31 add case screw holes
    [OpenHardwareHolterMonitor_case.scad]
2019-09-21 increase clearance based on prototype
    [OpenHardwareHolterMonitor_case.scad]
2019-09-21 increase tolerances
    [OpenHardwareHolterMonitor_case.scad]
2019-09-21 slope case bottom
    [OpenHardwareHolterMonitor_case.scad]
2019-09-21 round the corners
    [OpenHardwareHolterMonitor_case.scad]
2019-09-21 increase hex counter-sinks
    [OpenHardwareHolterMonitor_case.scad]
2019-09-21 widen screw holes
    [OpenHardwareHolterMonitor_case.scad]
2019-09-21 linebreaks on very long lines
    [OpenHardwareHolterMonitor_case.scad]
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2019-10-26 add pull-up resistors to EN and IO0
    [OpenHardwareHolterMonitor.kicad_pcb, OpenHardwareHolterMonitor.sch]
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

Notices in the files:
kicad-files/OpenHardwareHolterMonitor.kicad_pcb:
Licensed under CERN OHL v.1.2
